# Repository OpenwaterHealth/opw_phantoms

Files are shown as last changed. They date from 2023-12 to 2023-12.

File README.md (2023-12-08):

# opw_phantoms
## Phantoms for Optical, Ultrasound, and Acousto-Optic Devices

Openwater has developed several phantoms for use with our optical, ultrasound, and acousto-optic devices. These phantoms are designed to simulate the characteristics of interacting tissue, and have various formulations and mechanical configurations depending on the application. 

## Prerequisites and Usage

See the repo Wiki for detailed instructions for preparation and usage of phantoms. 

## Repository Contents
Recipes and mechanical design data for 
- [optical system phantoms](optical)
- [ultrasound system phantoms](ultrasound_and_AO)
- [acousto-optic system phantoms](ultrasound_and_AO)

## Contributing

We welcome contributions from the community. If you have ideas for improvements or find any issues, please open an issue or submit a pull request.

Before contributing, please read our [Contributing Guidelines](CONTRIBUTING.md).

## License
opw_phantoms is licensed under the GNU Affero General Public License v3.0. See [LICENSE](LICENSE) for details.

## Investigational Use Only
CAUTION - Investigational device. Limited by Federal (or United States) law to investigational use. opw_phantoms has *not* been evaluated by the FDA and is not designed for the treatment or diagnosis of any disease. It is provided AS-IS, with no warranties. User assumes all liability and responsibility for identifying and mitigating risks associated with using this software.

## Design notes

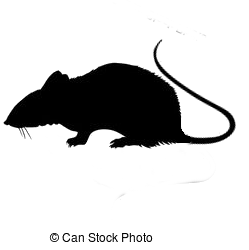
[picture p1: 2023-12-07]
ultrasound_and_AO/Rat_and_vein_phantoms/ratus_tailmove.png

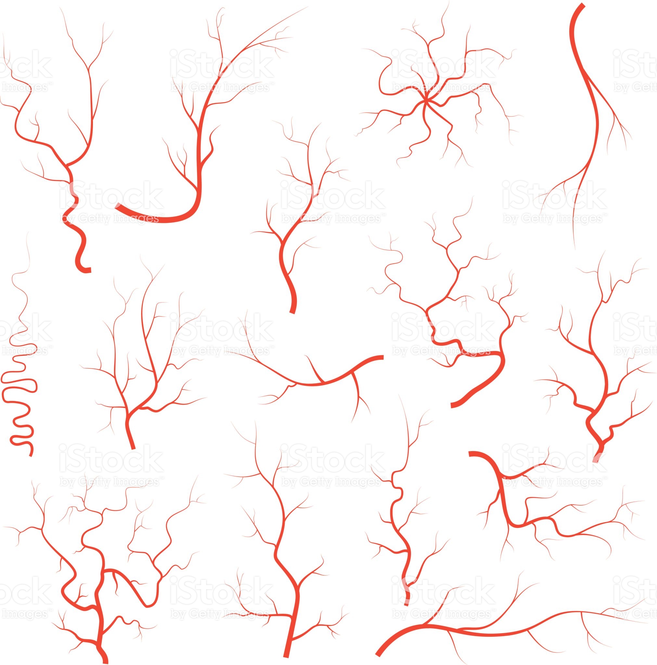
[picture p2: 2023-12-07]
ultrasound_and_AO/Rat_and_vein_phantoms/veinsarteries.jpg

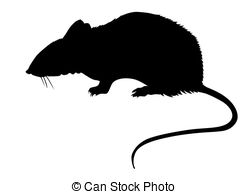
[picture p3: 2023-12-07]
ultrasound_and_AO/Rat_and_vein_phantoms/tatus.jpg

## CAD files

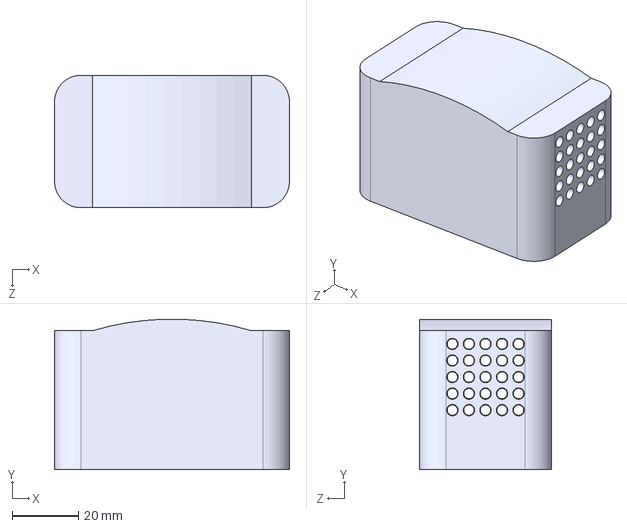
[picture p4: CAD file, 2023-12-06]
optical/flow_phantom/Flow Phantom Universal.STEP
71.0 x 45.5 x 40.0 mm

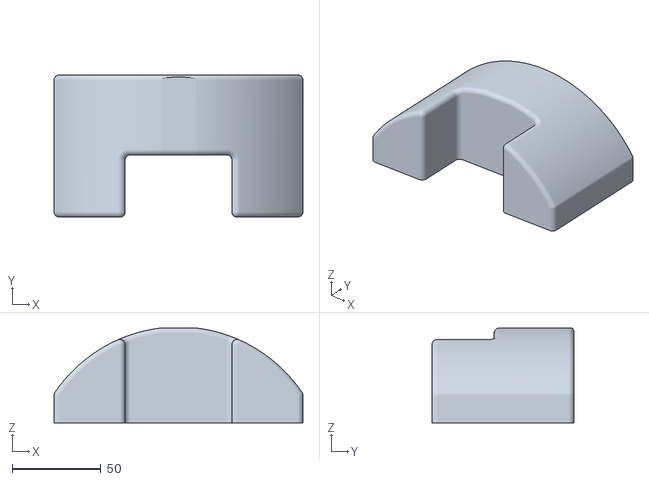
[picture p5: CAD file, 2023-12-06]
optical/static_phantoms/phantom_design/3000-0617 - PHANTOM, GEN 2 HEADSET - R02.STL
140.0 x 80.0 x 53.4

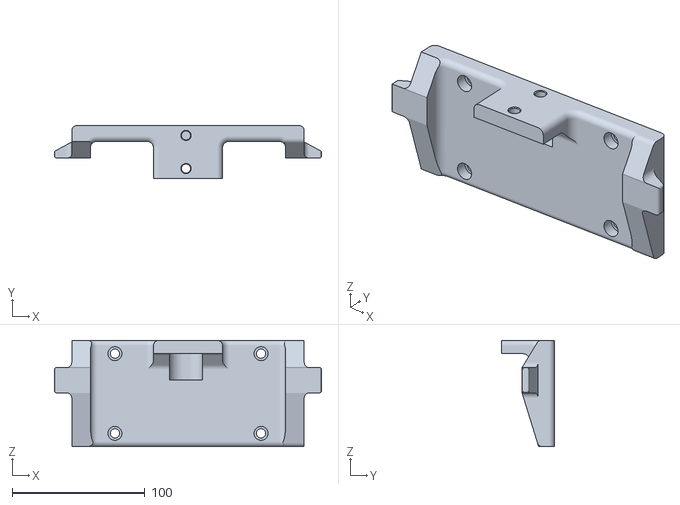
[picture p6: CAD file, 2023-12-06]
optical/static_phantoms/phantom_design/3000-0660 - MOUNT, PHANTOM - R01.STL
201.0 x 40.0 x 80.0

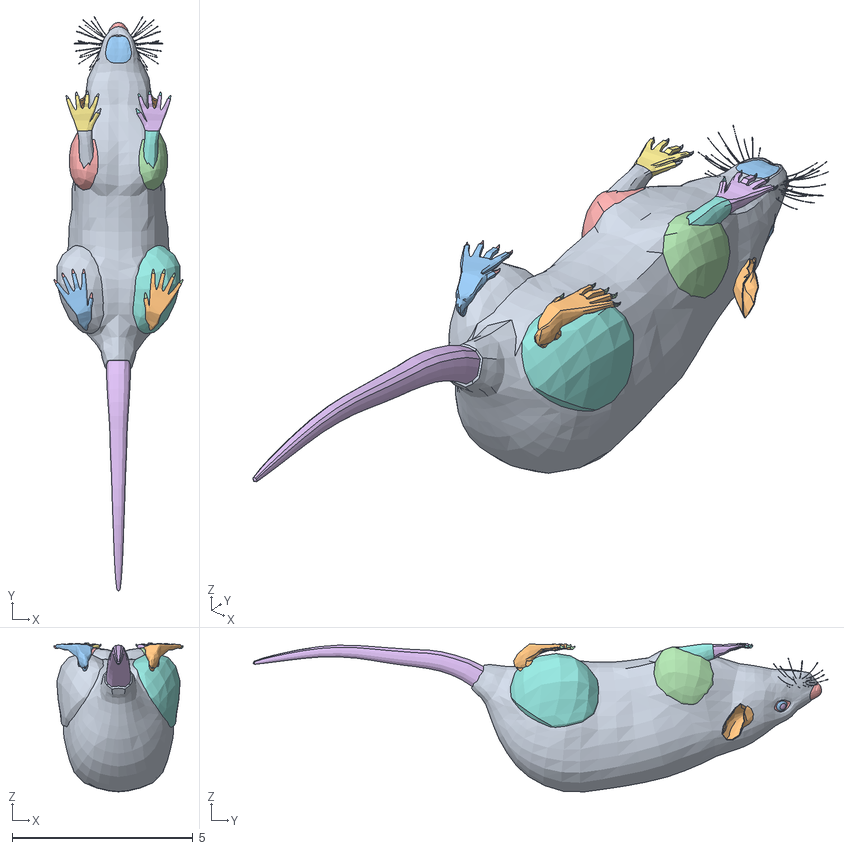
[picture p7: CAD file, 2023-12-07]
ultrasound_and_AO/Rat_and_vein_phantoms/4621_Rat/4621_Rat.obj
3.56 x 15.9 x 4.11
ear01
eyeballl01
eyeballr01
eyelids01
eyepupll01
eyepuplr01
forearml01
forearmr01
ftforel01
ftforer01
ftnaill01
ftnailr01
gumsdn01
gumsup01
hipl01
hipr01
jawgums01
jawhair01
jntankll01
jntanklr01
jntarml01
jntarmr01
jntjaw01
jntkneel01
jntkneer01
jntpawl01
jntpawr01
nose01
pawforel01
pawforer01
pawnaill01
pawnailr01
shinl01
shinr01
shldrl01
shldrr01
tail01
tongue01
tthfrtdn01
tthfrtup01
tthsiddn01
tthsidup01
upgums01
whiskers01

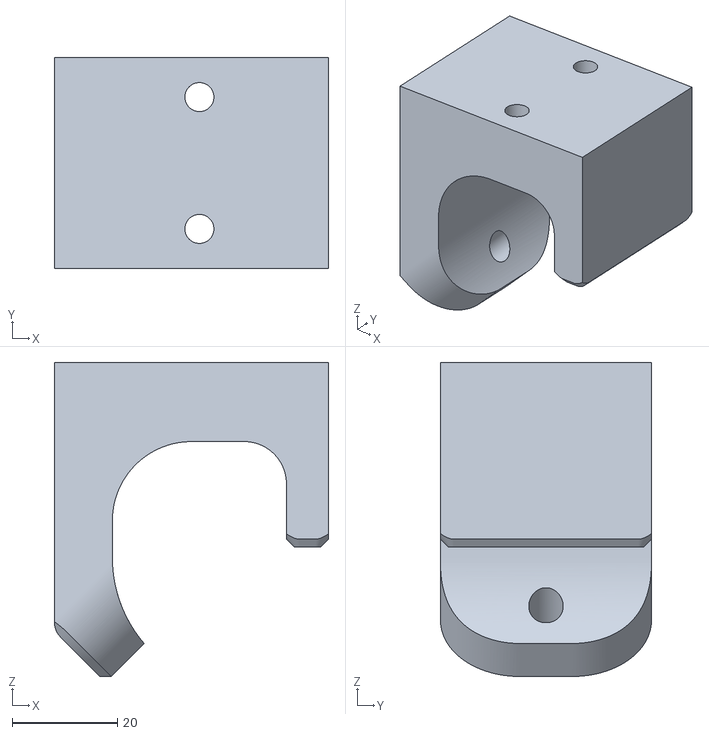
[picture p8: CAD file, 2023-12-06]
optical/static_phantoms/phantom_design/3000-0479 - POLE CLAMP - R01.STL
52.0 x 40.0 x 59.5

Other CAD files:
ultrasound_and_AO/Rat_and_vein_phantoms/4621_Rat/rat1.stp
ultrasound_and_AO/Rat_and_vein_phantoms/4621_Rat/rat.3dm
ultrasound_and_AO/Rat_and_vein_phantoms/4621_Rat/rat1.3dm
ultrasound_and_AO/Rat_and_vein_phantoms/4621_Rat/rat1.stl
ultrasound_and_AO/Rat_and_vein_phantoms/target mold 001.3dm
ultrasound_and_AO/Rat_and_vein_phantoms/target mold.3dm
ultrasound_and_AO/Rat_and_vein_phantoms/target moldx3 001.3dm
ultrasound_and_AO/Rat_and_vein_phantoms/target moldx3 002.3dm
ultrasound_and_AO/Rat_and_vein_phantoms/target moldx3.3dm
ultrasound_and_AO/Rat_and_vein_phantoms/targetmold3 001.3dm
ultrasound_and_AO/Rat_and_vein_phantoms/targetmold3.3dm

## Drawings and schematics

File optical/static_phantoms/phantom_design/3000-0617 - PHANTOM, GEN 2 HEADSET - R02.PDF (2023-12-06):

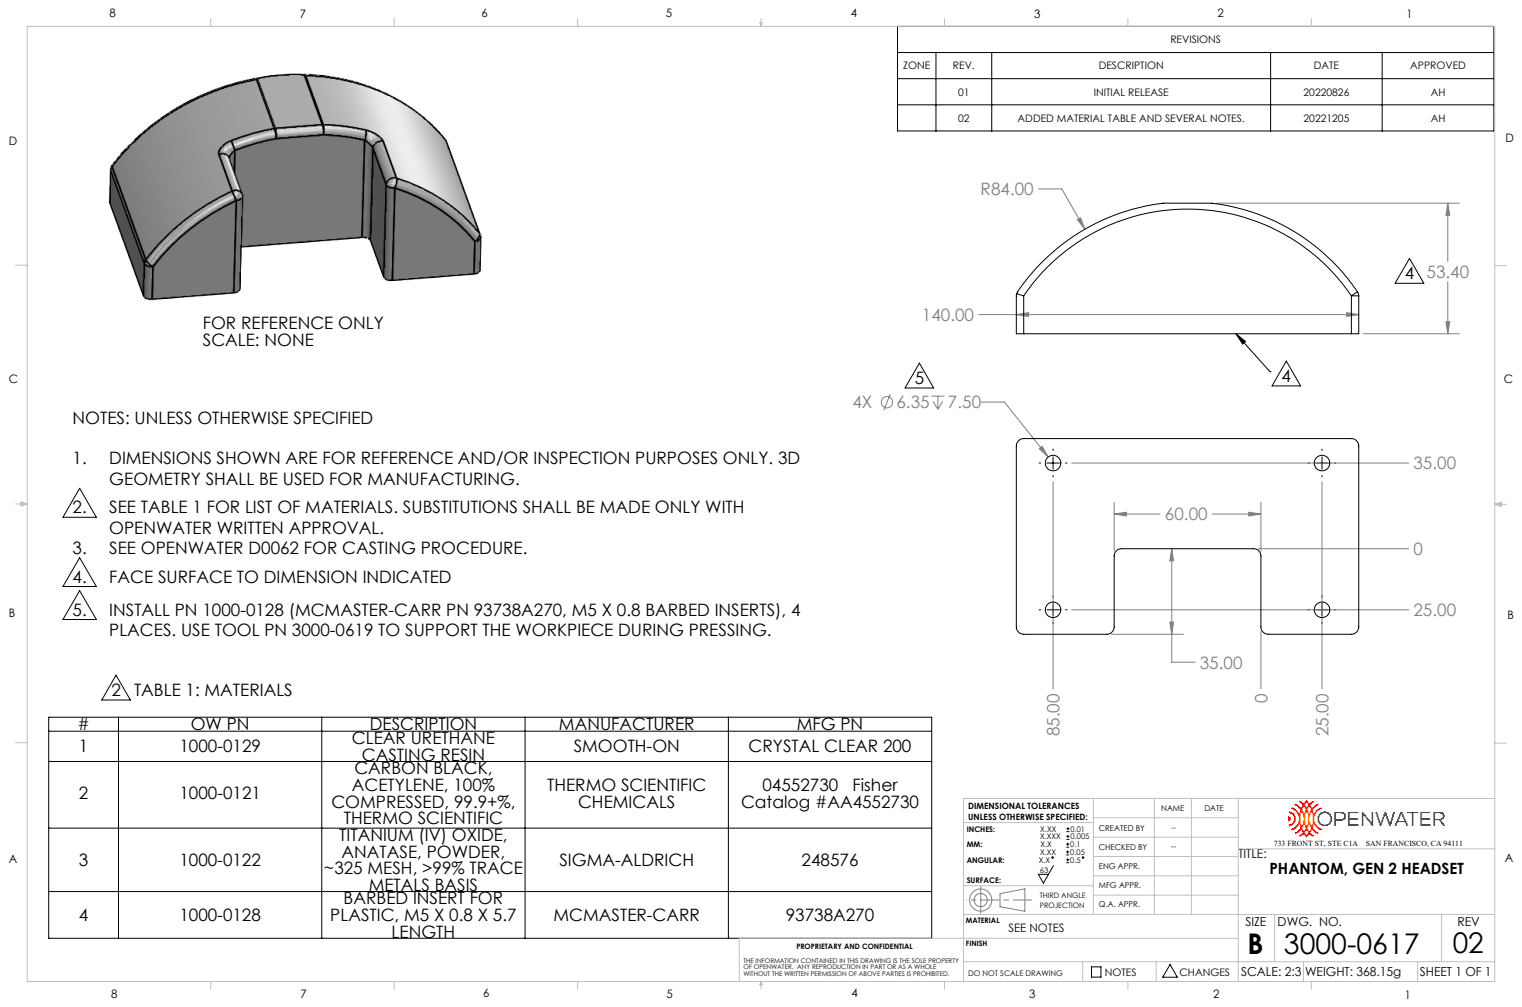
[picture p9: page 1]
2 TABLE 1: MATERIALS; INITIAL RELEASE; ADDED MATERIAL TABLE AND SEVERAL NOTES.; X.XXX 0.005; THIRD ANGLE; SEE NOTES; CREATED BY; CHECKED BY; ENG APPR.; MFG APPR.; Q.A. APPR.; DWG. NO.; REV; SCALE: 2:3 WEIGHT: 368.15g; DO NOT SCALE DRAWING; SHEET 1 OF 1

FOR REFERENCE ONLY
SCALE: NONE

NOTES: UNLESS OTHERWISE SPECIFIED
1. DIMENSIONS SHOWN ARE FOR REFERENCE AND/OR INSPECTION PURPOSES ONLY. 3D
GEOMETRY SHALL BE USED FOR MANUFACTURING.
2. SEE TABLE 1 FOR LIST OF MATERIALS. SUBSTITUTIONS SHALL BE MADE ONLY WITH
OPENWATER WRITTEN APPROVAL.
3. SEE OPENWATER D0062 FOR CASTING PROCEDURE.
4. FACE SURFACE TO DIMENSION INDICATED
5. INSTALL PN 1000-0128 (MCMASTER-CARR PN 93738A270, M5 X 0.8 BARBED INSERTS), 4
PLACES. USE TOOL PN 3000-0619 TO SUPPORT THE WORKPIECE DURING PRESSING.

# | OW PN | DESCRIPTION | MANUFACTURER | MFG PN
1 | 1000-0129 | CLEAR URETHANE CASTING RESIN | SMOOTH-ON | CRYSTAL CLEAR 200
2 | 1000-0121 | CARBON BLACK, ACETYLENE, 100% COMPRESSED, 99.9+%, THERMO SCIENTIFIC | THERMO SCIENTIFIC CHEMICALS | 04552730 Fisher Catalog #AA4552730

DIMENSIONAL TOLERANCES
UNLESS OTHERWISE SPECIFIED:
SURFACE:

3 | 1000-0122 | TITANIUM (IV) OXIDE, ANATASE, POWDER, ~325 MESH, >99% TRACE METALS BASIS | SIGMA-ALDRICH | 248576

733 FRONT ST, STE C1A SAN FRANCISCO, CA 94111
TITLE:
PHANTOM, GEN 2 HEADSET

4 | 1000-0128 | BARBED INSERT FOR PLASTIC, M5 X 0.8 X 5.7 LENGTH | MCMASTER-CARR | 93738A270

PROPRIETARY AND CONFIDENTIAL

THE INFORMATION CONTAINED IN THIS DRAWING IS THE SOLE PROPERTY
OF OPENWATER. ANY REPRODUCTION IN PART OR AS A WHOLE
WITHOUT THE WRITTEN PERMISSION OF ABOVE PARTIES IS PROHIBITED.

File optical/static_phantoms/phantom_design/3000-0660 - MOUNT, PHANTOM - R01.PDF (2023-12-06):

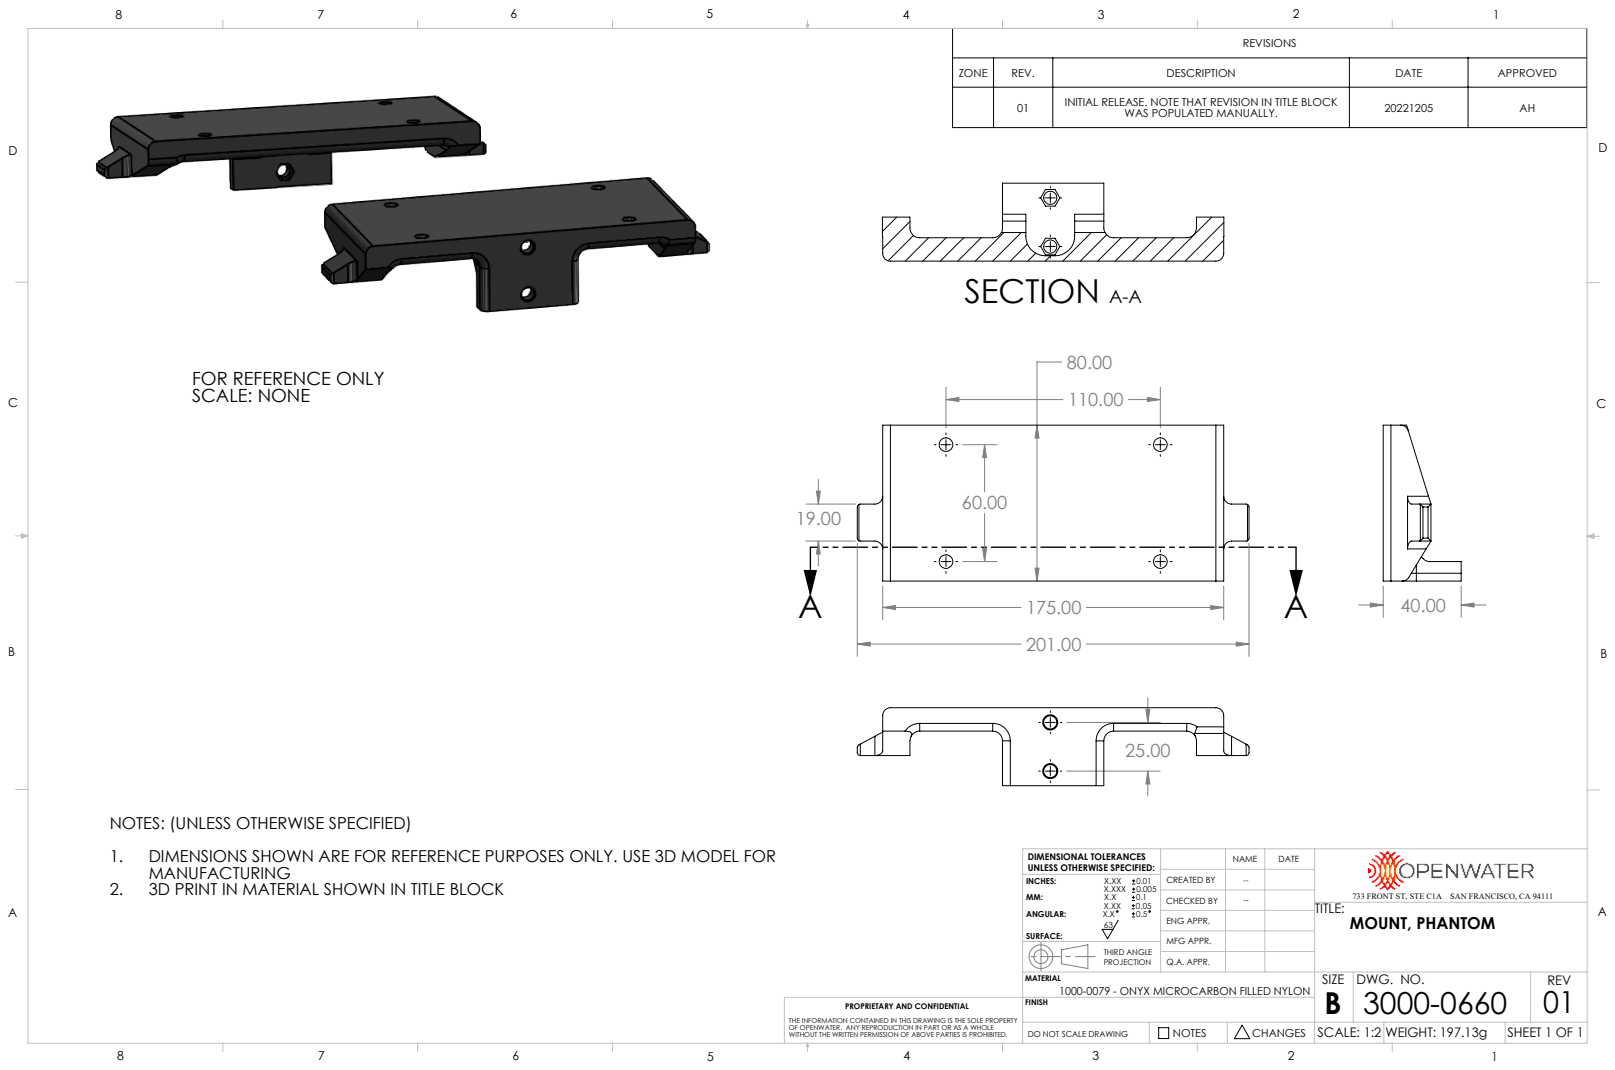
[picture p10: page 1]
SECTION A-A; INITIAL RELEASE. NOTE THAT REVISION IN TITLE BLOCK; WAS POPULATED MANUALLY.; X.XXX 0.005; CREATED BY; CHECKED BY; ENG APPR.; MFG APPR.; Q.A. APPR.; DWG. NO.; REV; SCALE: 1:2 WEIGHT: 197.13g; DO NOT SCALE DRAWING; SHEET 1 OF 1

FOR REFERENCE ONLY
SCALE: NONE

NOTES: (UNLESS OTHERWISE SPECIFIED)
1. DIMENSIONS SHOWN ARE FOR REFERENCE PURPOSES ONLY. USE 3D MODEL FOR
MANUFACTURING
2. 3D PRINT IN MATERIAL SHOWN IN TITLE BLOCK

DIMENSIONAL TOLERANCES
UNLESS OTHERWISE SPECIFIED:
SURFACE:

733 FRONT ST, STE C1A SAN FRANCISCO, CA 94111
TITLE:
MOUNT, PHANTOM

THIRD ANGLE
PROJECTION
1000-0079 - ONYX MICROCARBON FILLED NYLON

PROPRIETARY AND CONFIDENTIAL

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

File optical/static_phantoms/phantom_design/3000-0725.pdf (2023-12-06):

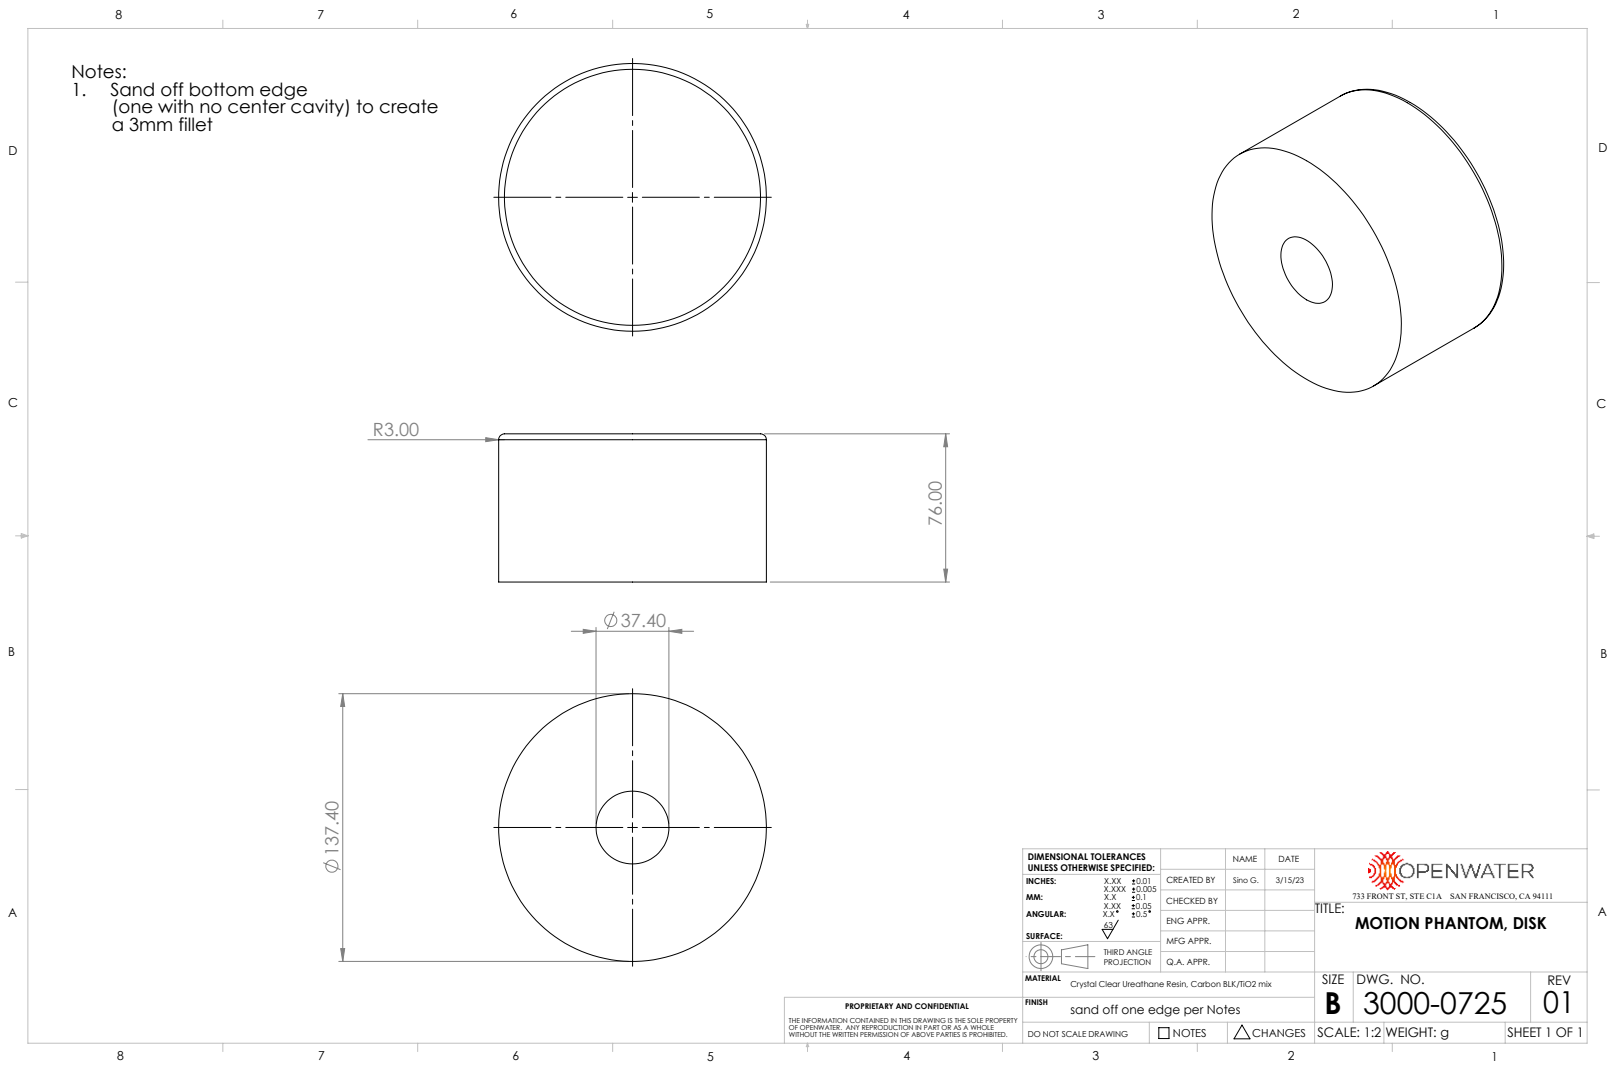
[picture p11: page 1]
X.XXX 0.005; THIRD ANGLE; CREATED BY; CHECKED BY; ENG APPR.; MFG APPR.; Q.A. APPR.; DWG. NO.; REV; SCALE: 1:2 WEIGHT: g; MOTION PHANTOM, DISK; DO NOT SCALE DRAWING; SHEET 1 OF 1; Sino G.

Notes:
1. Sand off bottom edge
(one with no center cavity) to create
a 3mm fillet

DIMENSIONAL TOLERANCES
UNLESS OTHERWISE SPECIFIED:
SURFACE:

733 FRONT ST, STE C1A SAN FRANCISCO, CA 94111

MATERIAL
sand off one edge per Notes

Crystal Clear Ureathane Resin, Carbon BLK/TiO2 mix

PROPRIETARY AND CONFIDENTIAL

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

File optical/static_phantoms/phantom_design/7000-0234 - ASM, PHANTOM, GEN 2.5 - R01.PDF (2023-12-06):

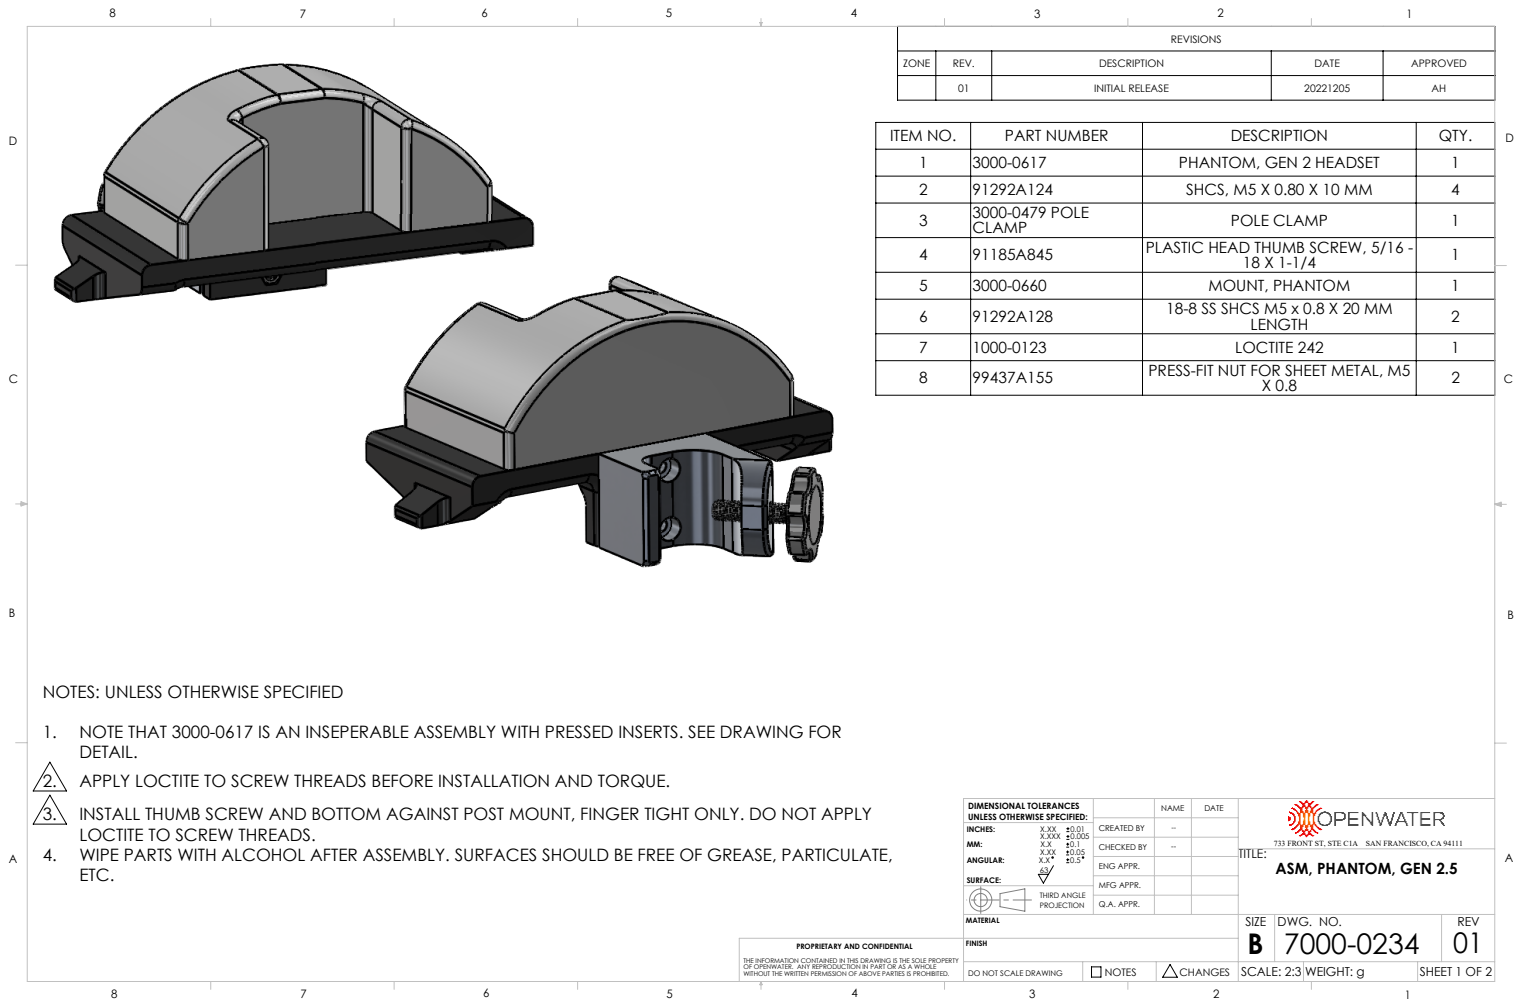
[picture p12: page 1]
INITIAL RELEASE; X.XXX 0.005; THIRD ANGLE; CREATED BY; CHECKED BY; ENG APPR.; MFG APPR.; Q.A. APPR.; DWG. NO.; REV; SCALE: 2:3 WEIGHT: g; DO NOT SCALE DRAWING; SHEET 1 OF 2

ITEM NO. | PART NUMBER | DESCRIPTION | QTY.
1 | 3000-0617 | PHANTOM, GEN 2 HEADSET | 1
2 | 91292A124 | SHCS, M5 X 0.80 X 10 MM | 4
3 | 3000-0479 POLE CLAMP | POLE CLAMP | 1
4 | 91185A845 | PLASTIC HEAD THUMB SCREW, 5/16 -18 X 1-1/4 | 1
5 | 3000-0660 | MOUNT, PHANTOM | 1
6 | 91292A128 | 18-8 SS SHCS M5 x 0.8 X 20 MM LENGTH | 2
7 | 1000-0123 | LOCTITE 242 | 1
8 | 99437A155 | PRESS-FIT NUT FOR SHEET METAL, M5 X 0.8 | 2

NOTES: UNLESS OTHERWISE SPECIFIED
1. NOTE THAT 3000-0617 IS AN INSEPERABLE ASSEMBLY WITH PRESSED INSERTS. SEE DRAWING FOR
DETAIL.
2. APPLY LOCTITE TO SCREW THREADS BEFORE INSTALLATION AND TORQUE.
3. INSTALL THUMB SCREW AND BOTTOM AGAINST POST MOUNT, FINGER TIGHT ONLY. DO NOT APPLY
LOCTITE TO SCREW THREADS.
4. WIPE PARTS WITH ALCOHOL AFTER ASSEMBLY. SURFACES SHOULD BE FREE OF GREASE, PARTICULATE,

DIMENSIONAL TOLERANCES
UNLESS OTHERWISE SPECIFIED:
SURFACE:

733 FRONT ST, STE C1A SAN FRANCISCO, CA 94111
TITLE:
ASM, PHANTOM, GEN 2.5

PROPRIETARY AND CONFIDENTIAL

THE INFORMATION CONTAINED IN THIS DRAWING IS THE SOLE PROPERTY
OF OPENWATER. ANY REPRODUCTION IN PART OR AS A WHOLE
WITHOUT THE WRITTEN PERMISSION OF ABOVE PARTIES IS PROHIBITED.

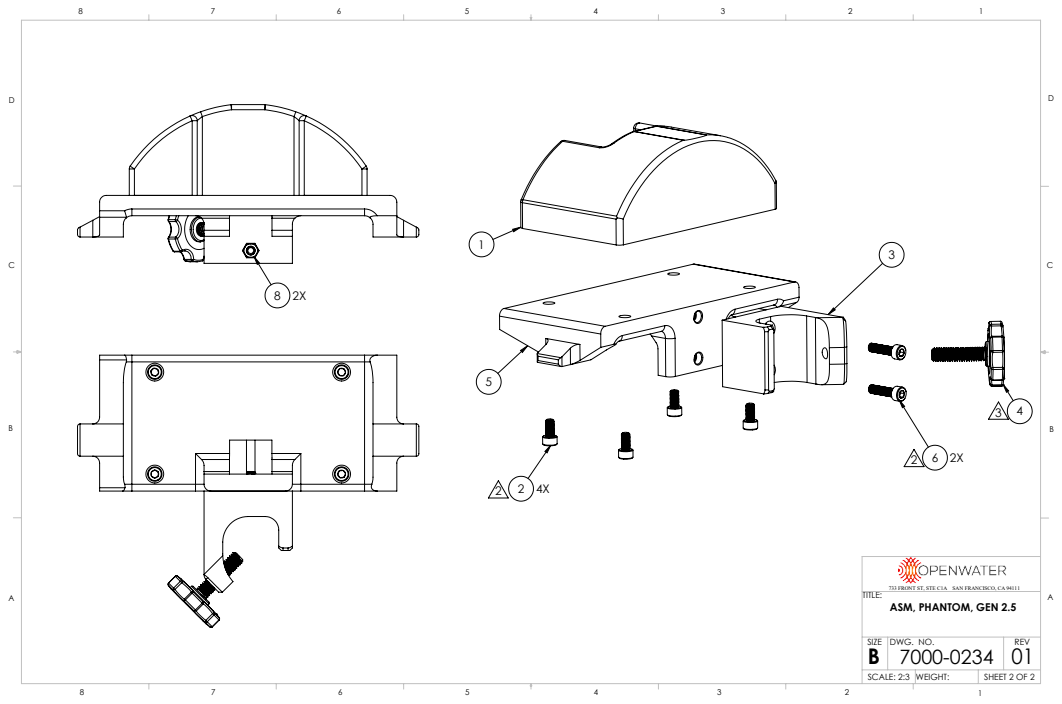
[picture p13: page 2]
DWG. NO.; REV; SCALE: 2:3 WEIGHT:; SHEET 2 OF 2

733 FRONT ST, STE C1A SAN FRANCISCO, CA 94111
TITLE:
ASM, PHANTOM, GEN 2.5

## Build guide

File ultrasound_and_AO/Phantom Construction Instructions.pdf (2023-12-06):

Acrylic Phantom Frames
- Use 5 total (alternating 3 without baffles, 2 with baffles)
- Use acrylic cement (dichloromethane) to attach 5 frames together
- Make sure that they are squared up, otherwise they may not fit in tanks
- Use something underneath frames during this process so that they don’t cure to working surface
- Attach wooden cotton-tipped applicators to acrylic frame with UV-curing cement if desired
- Frames are from TAP Plastics, ask Wilson to order more
- Give frames an assembly number per the Built Phantom List and Specs. Ideally label the frame on all three sides and engrave at least one of these. Please touch base with Wilson and/or Brad if you have any questions.

GelWax
- Melt gelwax on medium to high heat, stirring occasionally
- 200-250 g are needed per phantom
- There should be two marker dots on heater to shoot for that will keep it warm but not smoking too much
- Use thermometer to check temperature ideally
■ 190°F (88C) = molasses/honey
■ 235°F (107C) = melted ice cream
■ 280°F (127C) = water
- Heating to at least 280°F and letting sit for a few minutes without any agitation should adequately degas the gelwax
- Add in all of the TiO2 mixture. To be on the safe side, it is preferable to pour a bit of the molten gelwax into the empty mineral oil/TiO2 cup in order to ‘rinse’ it out and extract as much of the TiO2 as possible.
- Mix TiO2

in mineral oil at ~0.4 g/g (use lower ratio if too difficult to dissolve, ideally you want to use as little mineral oil as possible)
- Sonicate mixture in bath for at least 10 minutes, stirring occasionally to make sure larger particles on side get mixed in and broken up
- Gelwax’s density at room temperatures is 0.856 g/mL
- Use recently cleaned acrylic or glass under frame to seal bottom
- Edges don’t need to be taped, as the gelwax will cool and solidify rapidly as it tries to fill in any cracks
- Use a thin layer of mineral oil as release agent on anything you don’t want gelwax sticking to
- If using cotton-tipped applicators, you may find it worth it to keep heating the top of the phantom with the heat gun in order to keep the gelwax molten. The cotton-tipped applicators will slowly be impregnated with gelwax and subsequently release lots of small air bubbles into the gelwax; so keeping the gelwax molten will allow more of the air bubbles to rise to the surface and pop. This can take 10-15 minutes or more.

- A better alternative would be to fully impregnate the cotton-tipped applicators while melting the gelwax, and then figure out a way to securely mount them in the frame before pouring all the gelwax in.
- Be sure to let the entire frame cool to room temperature before attempting to remove; doing it while warm can cause the gelwax to tear apart.

PDMS
- Mixing
- Weigh out, 1:10 is standard ratio (curing agent : PDMS Monomer)
■ Up to 1:40 for softer/tackier
- Add any absorbers/scatterers to the curing agent first, then use sonication bath
- to help break up the small particles.
- Degas for 5-10 minutes in vacuum chamber before/after pouring into mold. Best results will occur when using a large container so that you can let the vacuum go to it’s max without the mixture overflowing.
- Curing
- Release agent
■ Generally not needed, is mostly the case if using brand new glass or acrylic
■ If using glass or acrylic, make sure that it is extremely clean (use strong cleaners or solvents to get off any remaining residue)
■ If you do use a release agent, make sure to let it fully dry (at least 30 minutes) before casting as it can inhibit the curing process.
- Can decrease cure time by putting in oven at 50-70C
■ For higher ratios (e.g. 1:40) may be better to let cure at room temperature first, then final cure for 1-2 hours in the oven (higher ratios may take longer to cure in general).
■ Note: The warmth of the oven may cause excessive leaking of the PDMS, notably from joints which didn’t leak at room temperature.
■ Unless mold is completely water-tight, suggest to let it cure overnight and then bake for 1-2 hours once it has thickened up.
- If cure inhibition (tackiness/stickiness) occurs, can heat up surface with blow torch (tested) or possibly bake at high temperature in oven (not tested)

Dragon Skin 20
- Make sure to mix each container thoroughly before using, some component of it seems to settle at the bottom
- ¼” acrylic stirring sticks work okay, just make sure to dull edge, otherwise creates plastic shreds from scraping inside of bucket (if too many shreds form, they tend to float to the top over a day or two and can be skimmed off the surface)
- Using a release agent helped a bit, it didn’t seem to stick too badly to the acrylic though even without using it

- Pot seemed to be a bit longer than the advertised 25 minutes; closer to 40 minutes from my experience
- Despite this, you are still best off degassing the mixture as rapidly as possible. Generally I wouldn’t waste time going through more than one vacuum cycle.

Optical Properties
- TiO2
- Typically at 0.72 g/L (equivalent of μs = 1 cm⁻¹ = 0.1 mm⁻¹
)
- Ivory Black
- 0.028 g/L (equivalent of μa = 0.1 cm⁻¹ = 0.01 mm⁻¹
)

Liquid Scattering Phantom
- Scattering
- Half and half milk
■ Lucerne Brand:
- 75 g/L or 7.5% (equivalent of μsp

’ = 1 mm⁻¹
)
■ Clover Brand:
- 72.5 g/L or 7.25% (equivalent of μsp

’ = 1 mm⁻¹
)
■ Horizon Organic Brand:
- 70 g/L or 7.0% (equivalent of μsp

’ = 1 mm⁻¹
)
- Intralipid
■ I141-100 mL Intralipid, 20% Emulsion Intralipid:
- 32 g/L or 3.2% (equivalent of μsp

’ = 1 mm⁻¹
)
- Absorption
- India Ink
■ Higgins (non waterproof), diluted to 1%:
- 11.6 g/L or 1.16% (equivalent of μa = 0.016 mm⁻¹
)
■ Final concentration of India Ink in liquid phantom should be 0.116 g/kg
- Report & links to data: E0025 - Intralipid & India Ink Speckle Contrast Phantom
- Instructions
- Starting with water, add 7.5% of half and half by weight to get the right reduced scattering coeff of μsp

’ = 1 mm⁻¹
. (we are using a specific density of 1 => 1g=1ml). Then, use the 1% stock solution for india ink (again, 1g=1ml, 1% soln= 1g india ink, 99 ml water), and add enough to the scattering solution to make it 1.16% of initial soln.
■ The half and half (preferably Lucerne brand) is taken out of the refrigerator and kept at room temperature for 30 min prior to making the phantom.
- Example calculations (half & half):
■ If making about 1500 ml soln, add 112.5 g half and half to 1387.5 ml water to make 1500 ml total soln.

■ Then add 17.43 g of 1% stock solution of ink to the 1500 ml prepared scattering solution to make a total solution of 1517.43 ml (conc= 17.43/1500= 1.16%).
- With 20% intralipid, the right concentration is found through experimentation to be 3.2%. Then, use the 1% stock solution for india ink (again, 1g=1ml, 1% soln= 1g india ink, 99 ml water), and add enough to the scattering solution to make a 1.16% soln.
- Example calculations (intralipid):
■ If making about 1500 ml soln, add 48 g 20% Intralipid to 1452 ml water to make 1500 ml total soln.
■ Then add 17.43 g of 1% stock solution of ink to the 1500 ml prepared scattering solution to make a total solution of 1517.43 ml.

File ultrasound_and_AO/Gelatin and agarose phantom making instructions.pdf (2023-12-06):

# Phantom Making - Gelatin and Agarose

### June 1st, 2021

# Introduction

This document lists instructions for the fabrication of phantoms that vary in speed of sound and currently used for the Structural Imaging Project. The matrix materials are Gelatin and Agarose.

## Gelatin

Gelatin is a common phantom-making material due to its easy accessibility in most supermarkets. Although most non-flavored gelatin brands can be used in order to create ultrasound phantoms, different types of gelatin could result in different speeds of sound for the same concentration in relation to water and alcohol. It is preferable to maintain a single type of powdered gelatin for phantom fabrication for consistency.

### How to make phantoms

Ingredients: Powdered gelatin, tap water, and n-propyl alcohol
1. Decide on the percentage of gelatin in weight to the volume of liquid (water and n-propyl alcohol). Separate each of the ingredients.
2. Separate the volume of water to be used in two equal parts.
3. Mix the gelatin in powder to ½ of the water volume into a glass beaker and stir.
4. Microwave the water+gelatin mixture until bubbles are observed.
5. Mix the hot water+gelatin mixture with the room temperature remaining water and the alcohol.
6. Let it cool at room temperature or in the refrigerator.

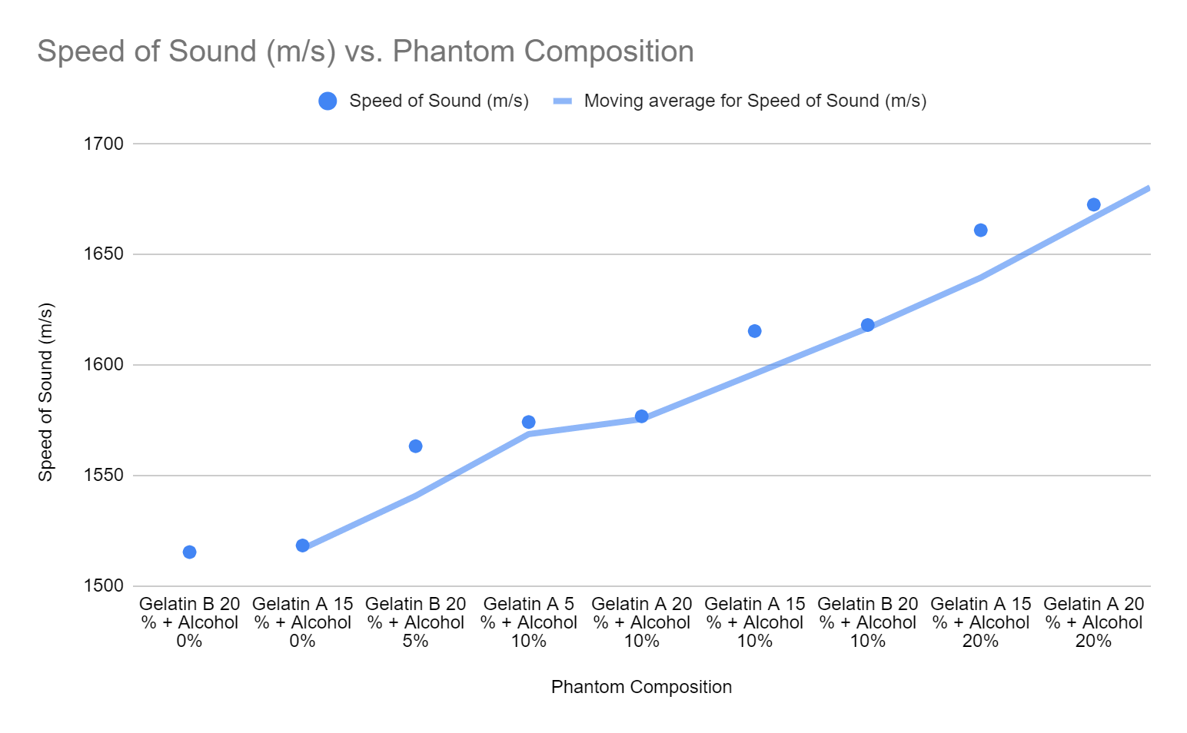
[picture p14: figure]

### Speed of Sound values

Phantom Composition | Speed of Sound (m/s)
Gelatin B 20 % + Alcohol 0% | 1515.215201
Gelatin A 15 % + Alcohol 0% | 1518.200841
Gelatin B 20 % + Alcohol 5% | 1563.161706
Gelatin A 5 % + Alcohol 10% | 1574.094419
Gelatin A 20 % + Alcohol 10% | 1576.685682
Gelatin A 15 % + Alcohol 10% | 1615.282845
Gelatin B 20 % + Alcohol 10% | 1618.014739
Gelatin A 15 % + Alcohol 20% | 1660.942447
Gelatin A 20 % + Alcohol 20% | 1672.500078

### Conservation

Preferrably gelatin should be kept in an airtight container. Wrapping the phantom in sarin wrap and placing inside a ziploc bag might reduce the risk of biological contamination/degradation, but the phantom should only last a few days. If placed in water, the phantom will swell due to osmosis and lose its acoustic properties previously defined.

## Agarose

### How to make phantoms

Ingredients: Quick dissolving agarose, tap water, and n-propyl alcohol
1. Decide on the percentage of agarose in weight to the volume of liquid (water and n-propyl alcohol). Separate each of the ingredients.
2. Mix the agarose in powder to ½ of the water volume into a glass beaker and stir.
3. Cover the beaker with paper towels and tape down
4. Microwave the water+agarose mixture until bubbles are observed.
a. Check the water level after microwaving, might need to correct for liquid evaporation
5. Let it cool at room temperature or in the refrigerator.

### Speed of Sound values

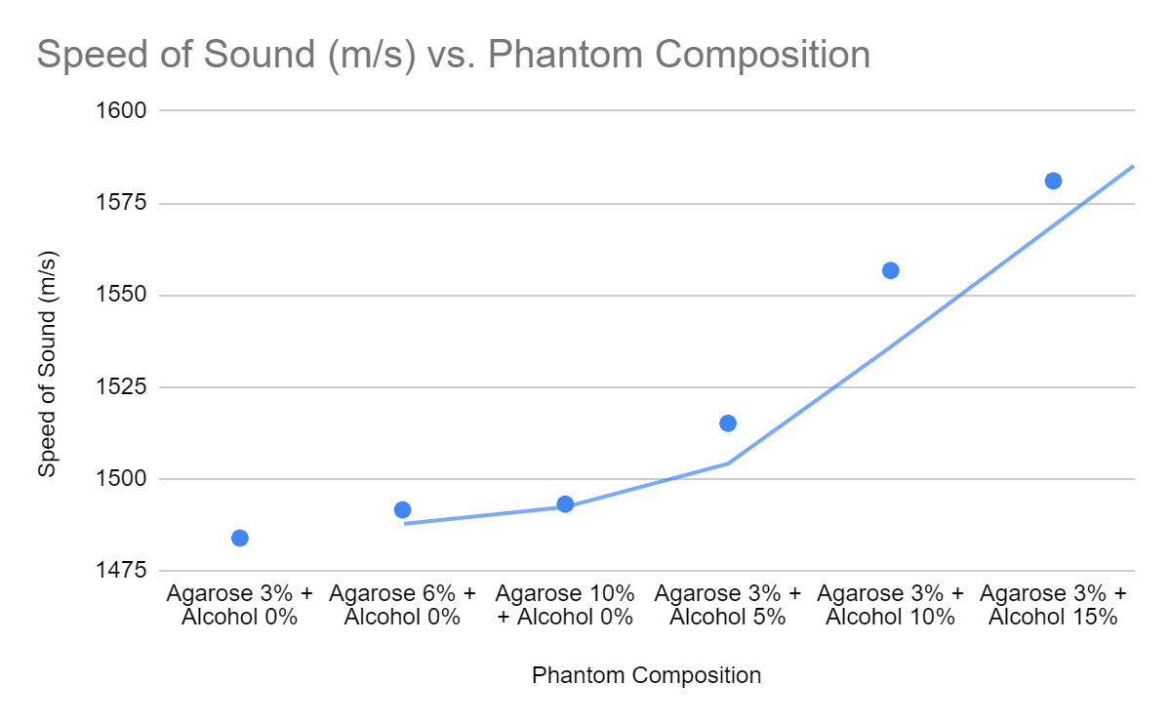
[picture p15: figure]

Phantom Composition | Speed of Sound (m/s)
Agarose 3% + Alcohol 0% | 1483.87
Agarose 6% + Alcohol 0% | 1491.54
Agarose 10% + Alcohol 0% | 1493.1
Agarose 3% + Alcohol 5% | 1515.073401
Agarose 3% + Alcohol 10% | 1556.638373
Agarose 3% + Alcohol 15% | 1581.013244

### Conservation

Agarose is preferable over gelatin due to its better outcome in preservation days after the phantoms is created. When placed in water, agarose can maintain its shape integrity for a few weeks.

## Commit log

2023-12-06 updated folder names
    [3000-0479 - POLE CLAMP - R01.STL, 3000-0617 - PHANTOM, GEN 2 HEADSET - R02.STL, 3000-0660 - MOUNT, PHANTOM - R01.STL, Flow Phantom Universal.STEP]
2023-12-07 added rat and vein phantom files
    [4621_Rat.obj, rat.3dm, rat1.3dm, rat1.stl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]
